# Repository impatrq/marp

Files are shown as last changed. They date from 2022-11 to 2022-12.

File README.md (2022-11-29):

<div align="center">

# Mechanical Aid Rehabilitation Prototype

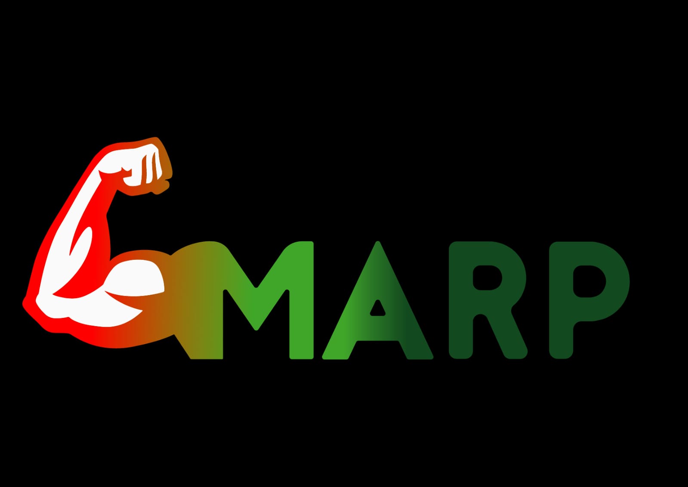
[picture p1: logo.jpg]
Logo proyecto


## ¿En qué consiste?

#### M.A.R.P (Mechanical Aid Rehabilitation Prototype) es un prototipo de exoesqueleto mecanico que consiste en un sistema de servomecanismos mediante el cual se obtiene un movimiento análogo a la contraccion de la mano. Estos son controlados por un microcontrolador. Tras recibir las señales de los musculos sensados por los electrodos colocados en el brazo, este activaria el protocolo correspondiente para realizar el movimiento deseado. En un principio este movimiento sera abrir y cerrar la mano.

## ¿Cuál es nuestro objetivo?

#### El objetivo de M.A.R.P. es asistir fisicamente a personas cuya capacidad motriz ha sido reducida, ya sea por haber sufrido daño nervioso y/o deterioro natural.

## ¿Quienes somos?

#### Somos un entusiasta grupo de 6 alumnos que se encuentran cursando el último año en la Escuela de Educación Secundaria Técnica N°7 (con especialidad en Aviónica) interesados en temas de medicina, biología y tecnología.

## Integrantes:

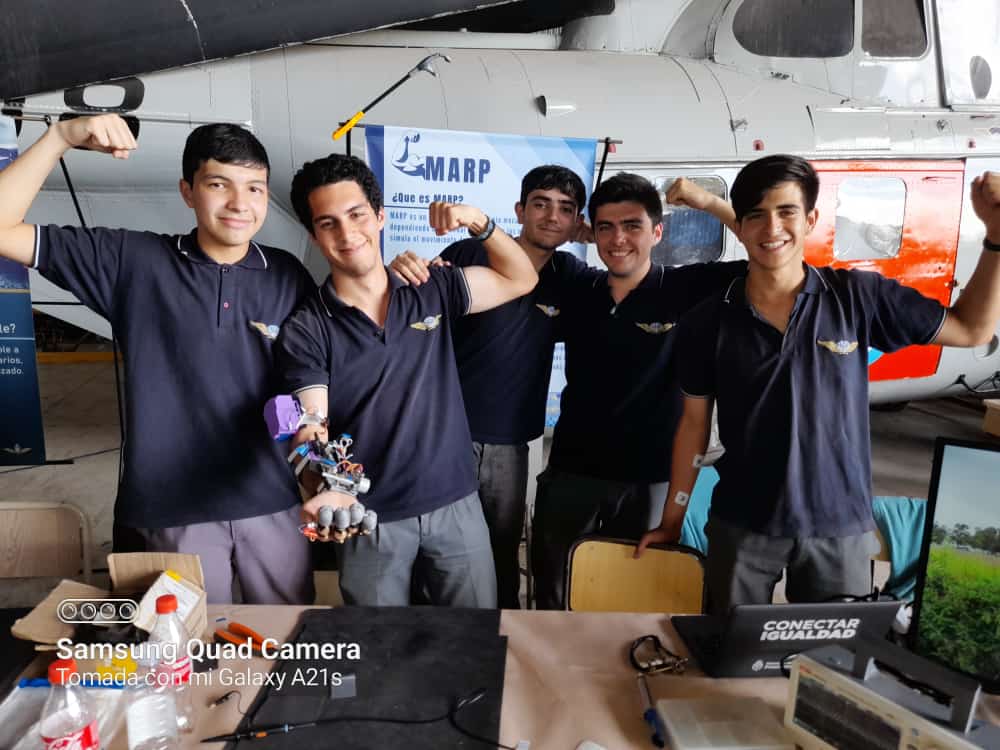
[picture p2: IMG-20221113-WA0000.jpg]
Integrantes


### NIETO, Matias Ezequiel
    📷 Instagram: matty_nieto
    📧 Email: mattynieto@gmail.com
### MONZÓN, Valentín Jeremias Daniel
    📷 Instagram: valen_monzii
    📧 Email: valenjereda10@gmail.com
### MONZON MATOS, Thomas Esteban 
    📷 Instagram: thomasmonzonmatos
    📧 Email: thomasemonzonm@gmail.com
### PIRILLO, Julian Dante 
    📷 Instagram: julianpirillo.03
    📧 Email: julipirillo@gmail.com
### FERNANDEZ IGLESIAS, Juan Ignacion
    📷 Instagram: juani.rvv
    📧 Email: juanignaciofernandez07@gmail.com
### LUPICA MARINI, Francisco Joaquin
    📷 Instagram: lupik_trq
    📧 Email: franciscolupica@gmail.com

## Contacto:
Cualquier duda la pueden consultar por:

    📧 Email: marpimpatrq@gmail.com
    📷 Instagram: marp_impatrq
    📞 Telefono: 1161022940

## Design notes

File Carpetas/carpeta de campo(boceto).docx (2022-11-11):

MARZO:

En este mes, presentamos una idea que ya teníamos desde el año pasado a nuestros profesores que era la de un exoesqueleto que ayudara a personas con poca o nula fuerza de agarre en labores cotidianos. Luego planteamos la idea actual del proyecto que sería un exoesqueleto capaz de ayudar a la rehabilitación de los nervios de la mano. Hubo cierta controversia debido a que uno de los profesores lo considero como uso ilegal de la medicina pero finalmente la idea fue aceptada y comenzamos a trabajar en el anteproyecto.

ABRIL:

En este mes se finalizo el anteproyecto anteproyecto, ya que había que finalizarlo para definir cuál sería nuestro proyecto (en el cual trabajaríamos el resto del año). Luego de varios debates e ideas, tanto para hablar del tema de costos hasta para pensar cómo funcionaría desde un punto de vista comercial, se pudo concluir la idea del exoesqueleto de mano. Antes de entregar el anteproyecto a nuestros profesores también dedicamos tiempo a hacer una investigación sobre las nociones básicas detrás de la obtención de señales electromiográficas. Esto incluiría como son producidas, de que magnitud son, en que consta el equipamiento encargado de recibirlas, como varían y según que, como poder aprovecharlas, etc. También investigamos y recibimos asesoramiento sobre el tipo de lesiones para las cuales el exoesqueleto sería útil incluyendo lesiones por daño nervioso, neuropatías periféricas o enfermedades neurodegenerativas e Incluso victimas de daño cerebral. Nuestro proyecto todavía recibía críticas por parte del profesor Bianco con respecto a su relación estrecha con la realización de procedimientos médicos sin ningún tipo de autorización o validez, pero el asunto quedo definitivamente zanjado para fin de mes al proponer nuestro proyecto como un prototipo a desarrollar mas que como un proyecto definitivo.

MAYO:

En este mes el anteproyecto ya fue aprobado y estábamos en condiciones de poder comenzar el proyecto. Empezamos a ver alternativas en internet sobre diferentes diseños, tanto del circuito de obtención de la señal como el exoesqueleto. Todos los circuitos que vimos para cumplir la función de obtener una señal clara de los músculos constaban de un amplificador diferencial de alta impedancia y bajo ruido con la siguiente estructura.

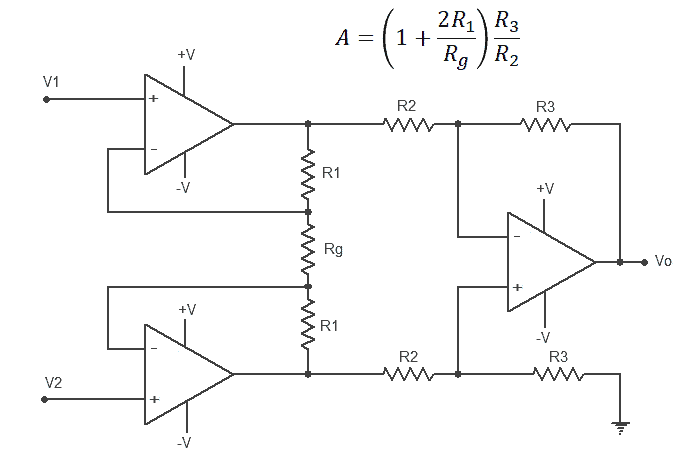
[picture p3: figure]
Instrumentation amplifier circuit diagram

La mayoría eran integrados INA106 el cual no pudimos conseguir por lo que tuvimos que reemplazarlo por un AD620. Este integrado fue diseñado específicamente para la obtención de señales electromiográficas. La ganancia de este amplificador se controla a través de una resistencia e hicimos los cálculos necesarios para obtener el valor que debería tener de manera que el AD620 tuviera una ganancia de 1000 veces el valor de la entrada. Esto se debe a que las señales del musculo son del orden de los 10 uV a los 100 mV, y para que funcione como condición para el Atmega328p que tenemos pensado utilizar, la señal final debe ser de 1V a 5V.

Para la etapa de filtrado tuvimos varios problemas. En parte se debía a que nadie sabía realmente cómo funcionaba un filtro y en parte porque en el lugar de trabajo donde en un futuro realizaríamos las primeras pruebas, había demasiado ruido. Al no saber el funcionamiento de los filtros nos limitamos a conseguir los materiales de uno de los circuitos que vimos y armarlo en un protoboard. También en este mes conseguimos los electrodos y la pasta conductora para iniciar las pruebas.

A pesar de que se nos recomendó trabajar por ahora únicamente en la obtención de la señal, se diseñaron bocetos de cómo podría llegar a ser el exoesqueleto. Dichos modelos incluyen un complejo sistema de engranajes para transformar el giro de un servo en el movimiento necesario para simular el cierre y apertura de la mano.

JUNIO:

En este mes se le empezó a dar importancia al tema del logo del proyecto. Se comenzó con bocetos en papel, y siguió con diseños completamente virtuales (todos se terminaron descartando).

Una vez armado sobre el protoboard nuestro primer circuito comenzamos con las pruebas. Tomó una cantidad absurda de tiempo invertido identificar ciertos errores que cometíamos en las mediciones sin estar conscientes de ello, ejemplo: no sabíamos que había que hacer una fuente partida, no sabíamos que la masa tenia que estar conectada a la masa del brazo. Tampoco sabíamos que el ruido en el ambiente podía ser tan fuerte como para atenuar la señal entregada y que eso se debía principalmente a la protoboard que actuaría como una antena y otros errores muy básicos, que en gran parte se deben a la falta de experiencia del grupo, que no vale la pena mencionar. Cambiamos el circuito pensando que los problemas se debían a la elección del mismo y primero intentamos hacer un tipo de filtro sallen key pasa bajo de Fc: 30Hz con la siguiente estructura.

(foto de filtro sallen key)

Comenzamos a entender mejor el principio de funcionamiento de un filtro por lo que sabíamos cómo calcular la frecuencia de corte y cómo funciona la atenuación de las señales. Sin embargo los filtros no funcionaron como deberían*

Nos limitamos a repetir la estructura del mismo filtro cuatro veces y lo que en proteus funcionaba a la perfección en la realidad funcionaba de manera muy distinta y no supimos por qué.

Sin embargo, tampoco sabemos por qué, cuando intentamos conectar al amplificador, únicamente un filtro Fc (el más básico que hay) pasa bajo con fc=100hz, se obtuvo el primer resultado positivo de todas las pruebas realizadas. Se apreció por primera vez una ligera pero constante variación en la señal obtenida a partir de los electrodos conectados al brazo del sujeto de prueba.

Desafortunadamente, la señal no era utilizable porque la variación era mínima, pero se amplificó, de los 10mV que suponemos que entrega el brazo, entregó 300 mV.

JULIO:

Este mes comenzamos a pensar y definir el sistema que utilizaríamos para mover los dedos de la mano, hicimos pruebas y comenzamos a diseñar el sistema en papel (el cual se cambio muchas veces). Acá fue cuando comenzamos a administrar la cuenta de instagram del proyecto para poder promocionarlo y que la gente lo conozca. Se reemplazó una parte del programador que ayudó a que los problemas de compatibilidad desaparecieran y se regresó a la programación.

También trabajamos junto al profesor Palmieri en la creación de una fuente partida pero en vez de utilizar las fuentes switching que usábamos antes utilizamos un transformador para obtener los +-5v que necesitábamos. Esto se decidió debido a que al trabajar con el profesor Arguello (y realizar nuestra primera prueba supervisada) nos advirtió que uno de los principales problemas de nuestro circuito era la propia fuente de alimentación. La propia masa de una fuente switching de por sí ya producía gran parte del ruido eléctrico. Fue ahí cuando supimos que debíamos utilizar o una batería o un transformador para evitar ese ruido.

(foto de la plaqueta)

El armado de las plaquetas y la prueba de la misma tuvieron varios inconvenientes. Entre ellos el hecho de que conectamos mal el regulador de la fuente (pensamos que un 7805 conectado al revés era lo mismo que un 7905) y quemamos varios fusibles, y también que las conexiones en si también estaban mal. Terminamos dejándolo de lado y planificamos la obtención de baterías electrolíticas para generar los +-5v.

Nuevamente volvimos a cambiar el circuito de filtrado esperando nuevamente que cambiarlo fuera suficiente para que dicho circuito funcionara.

(Foto del circuito)

Link de la página: https://www.dalcame.com/emg.html#.Y2JyHnbMLIU

Esta página también incluía información bastante detallada sobre el funcionamiento detrás de la electromiografía.

Esta vez sí nos tomamos el tiempo de aprender el funcionamiento detrás de cado de cada etapa del amplificador y filtrado.

Etapa de preamplificación:

(Foto amplificación)

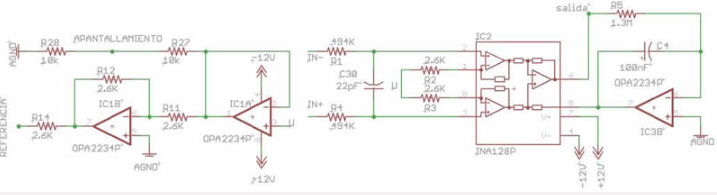
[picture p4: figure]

Esta etapa es la del AD620 pero también se incluía a la entrada positiva y negativa un filtro Rc. Esta vez el circuito incluía una etapa que era de apantallamiento que no sabemos para qué sirve pero aun así la incluimos. Se supone que aisla a la masa proveniente de los electrodos del resto del circuito. Obteniendo así supuestamente una señal con menos ruido y como son las pendientes de atenuación de la señal en base a la calidad del filtro

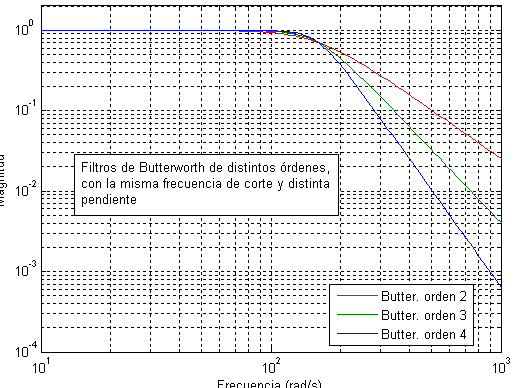
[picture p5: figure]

Primera etapa del filtro:

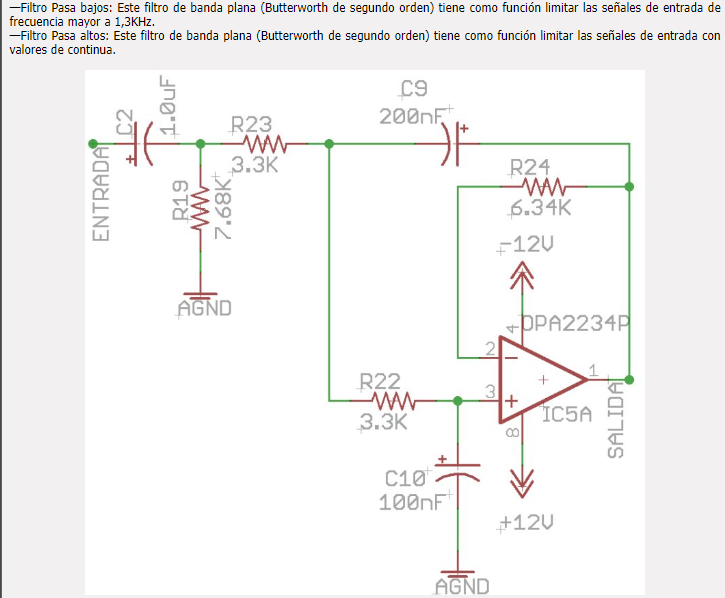
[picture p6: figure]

En el circuito a diferencia de los anteriores vistos tiene un filtro pasa bajos de 1.3KHz y pasa bajos de 1Hz butterworth. Y están diseñados de tal manera que la calidad del filtro sea mucho mayor

Esta era una de las posibles causas que anteriores filtros no funcionaran. Que la calidad del filtro varía según el valor de los elementos pasivos y que a pesar de que diferentes valores de los mismos podrían dar una frecuencia de corte similar el valor “Q”, que indica su calidad, no es el mismo. El valor para que el filtro sea de buena calidad de Q es 0.707.

Amplificacion

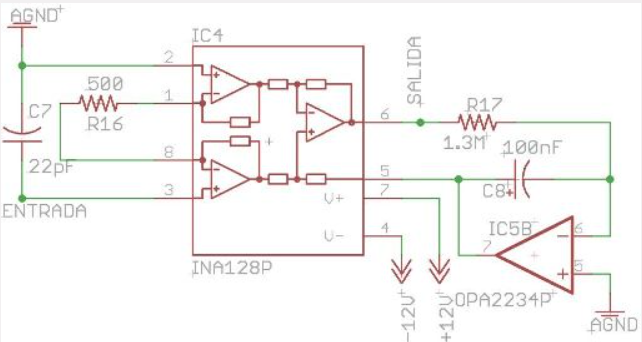
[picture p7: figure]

Este mes no se realizaron muchas pruebas por dos motivos: el primero serian las vacaciones de invierno, y el segundo es que hubo un retraso con el pedido de las baterías y decidimos dejar de realizar pruebas con las fuentes switching.

Como no podíamos hacer pruebas hasta obtener la batería le dedicamos mas tiempo a de una vez tener un modelo definitivo de la mano. Una vez obtenido supimos que gran parte de la misma tendría que ser diseñada en AutoCAD para su posterior impresión.

AGOSTO:

En este mes ya comenzamos a hacer la carcasa del proyecto en AutoCAD 3D, hicimos los soportes necesarios para las plaquetas, y el sistema de retracción de los dedos. Comenzamos la investigación sobre el programador y ya casi teníamos concluido el diseño logo.

SEPTIEMBRE:

En este mes continuamos con la obtención de materiales y conseguimos hacer funcionar el servo. También volvimos a cambiar por completo el circuito del filtro y con eso tuvimos que conseguir más materiales para su armado. Hicimos pruebas con este nuevo circuito y funcionaba cuando el input era un generador de seña. A la hora de conectarlo a un brazo no se podía obtener una buena señal (pésima relación signal to noise). También simulamos todo el circuito en proteus. En teoría funcionaria pero como resulta difícil agregar ruido en proteus no pudimos probar añadir más de una frecuencia. También imprimimos algunas de las partes de la mano.

OCTUBRE:

En este mes imprimimos en 3D las piezas de la carcasa en PLA y Flex. Como también rediseñar nuestro logo, y hacer el banner del proyecto para la exposición. También terminamos la programación del atmega328p para que mueva los servos que retraerán a los hilos, los cuales ayudaran a la mano a cerrarse y abrirse. A finales del mes se hizo la plaqueta del atmega328p en cobre, como también, la compra de un módulo con el AD620.

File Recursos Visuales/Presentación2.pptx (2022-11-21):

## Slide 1

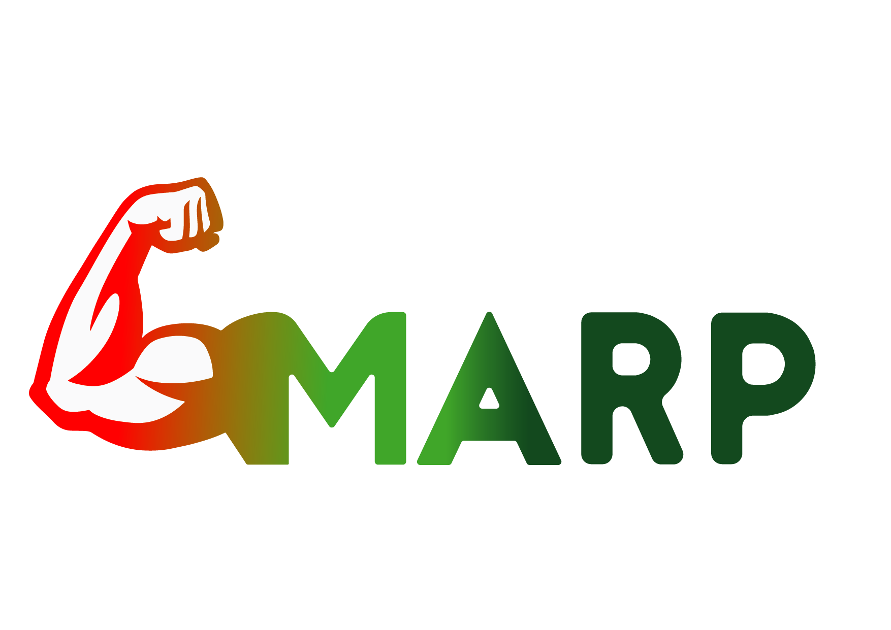
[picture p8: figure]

## ¿Qué es MARP?

- Mechanical Aid Rehabilitation Prototype (MARP) es un prototipo de instrumentación mecánica que se encarga de proveer la ayuda necesaria a la persona requerida cuya fuerza motriz fue debilitada por ciertos factores.

## ¿Cómo funciona?

- MARP utiliza señales eléctricas provocadas por la extensión y contracción muscular que son medidas con electrodos descartables
- Estas se envían a un amplificador y filtros para separar la señal del resto del ruido y hacerla detectable para el ATMEGA
- El Atmega328 P, es el corazón del proyecto, es quien da la orden a un motor Paso a Paso para que mueva los hilos de la carcaza y terminen por ayudar a contraer o extender los dedos de la mano

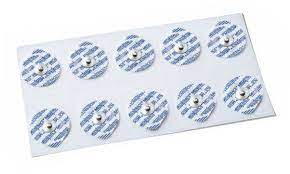
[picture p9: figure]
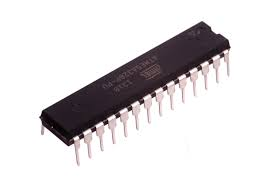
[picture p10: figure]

## Objetivo

- MARP se creó para brindar ayuda a las personas cuya movilidad o fuerza motriz fue reducida por un accidente u otros factores.
- Con MARP, los ejercicios de rehabilitación no serían obligatorios, ya que este produce la fuerza y efectos de igual manera para que el usuario pueda seguir con su vida cotidiana (La fuerza que brinda se irá reduciendo gradualmente hasta finalizar la rehabilitación)
- MARP no está diseñado para ser un añadido permanente al usuario, si no para apoyarlo en el transcurso de su recuperación.

## Procedimiento

Para la rehabilitación es necesario atravesar 4 fases:
- Fase de protección: confección de prótesis, manejo de edema y control del dolor.
- Fase restauradora: ejercicios de movilidad activa y de deslizamiento tendinoso.
- Fase de fortalecimiento: ejercicios de resistencia progresiva.
- Fase funcional: enfocada a recuperar habilidades para el desempeño de actividades de la vida diaria, tanto laborales como educativas.

## Integrantes

- MONZON MATOS, Thomas Esteban
- MONZÓN, Valentín Jeremias Daniel
- LUPICA MARINI , Francisco Joaquín
- NIETO, Matías Ezequiel
- PIRILLO, Julián Dante
- FERNÁNDEZ IGLESIAS, Juan Ignacio

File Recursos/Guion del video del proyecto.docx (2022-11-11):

Guion del video del proyecto:

Escena 1

- EXT. - Campo de aviónica superior.

Aparece peatón random (Francisco) mientras estaba bebiendo una Coca-Cola de 600 ml (mientras cruza panorámicamente la cámara fija), cuando de repente un balón de futbol impacta en dicha mano. Haciéndolo gemir de “dolor”.

- Fran: Arghhhhh. Mi mano, Hijos de p###.

En ese momento aparece caminado una persona (Juan) vestida con mercancía de marp/traje.

- Juan: Estas bien? No lo parece. Pero no te preocupes. Te presento marp.

*abre un maletín con el logo de marp (el interior no se verá desde el ángulo de la cámara)*

- Fran: Marp?

*comienza a desaparecer para luego desaparecer por completo*

Escena 2

- INT. – Sala secreta de MARP.

Aparece la persona (Fran) en una sala, confundido mira a su alrededor y encuentra en su delantera una mesa, con los integrantes de “MARP” (están usando mercancía de MARP) sentados en el lado opuesto de la mesa. Cuando la persona se da cuenta de su presencia un integrante dice:

- Valen: Bienvenido. ¿Te encuentras bien?

En ese momento se enfoca la cámara desde detrás de la persona un poco hacia arriba apuntando a la mesa, mientras se cae/rompe algo relacionado con MARP. Luego la cámara apunta a Fran:

- Fran: Creo que no, no puedo mover la mano.

La cámara sube un poco mostrando que todos están al lado de Fran.

- Nieto: Tenemos la solución a eso.
- Parillo: Te presentamos MARP (mientras saca un maletín con exoesqueleto)

Escena 3

- EXT. - Patio de la escuela

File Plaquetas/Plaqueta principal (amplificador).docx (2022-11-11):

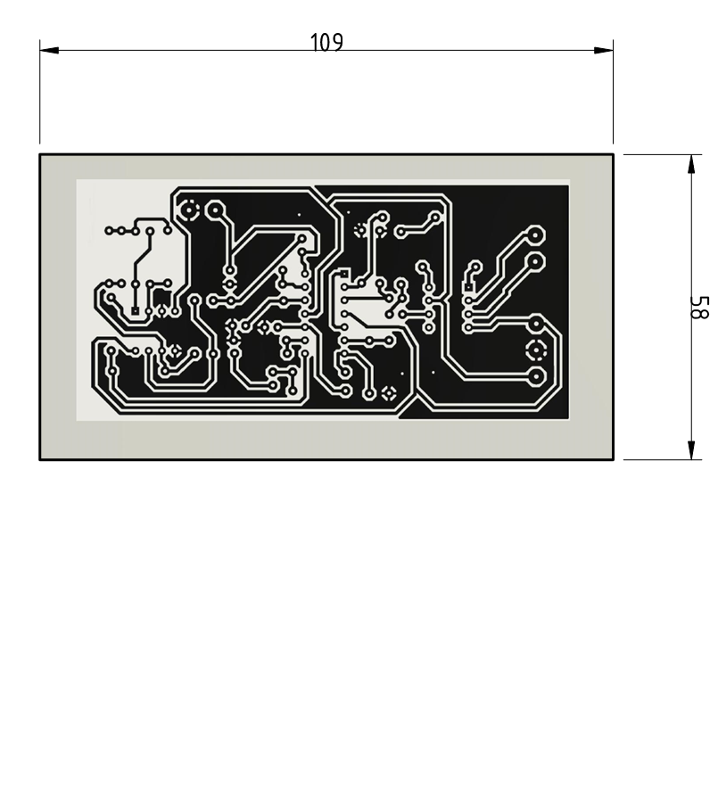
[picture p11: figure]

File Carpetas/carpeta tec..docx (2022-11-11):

Escuela de Educación Secundaria Técnica Nº7 TRQ

Proyecto final de 7mo

MECHANICAL
AID
REHABILITATION
PROTOTYPE

Integrantes:

FERNÁNDEZ, Juan Ignacio

LUPICA MARINI, Francisco Joaquín

MONZON MATOS, Thomas Esteban

MONZÓN, Valentín Jeremias Daniel

NIETO, Matías Ezequiel

PIRILLO, Julián Dante

## RESUMEN

Los diversos movimientos que podemos llegar a realizar con nuestro cuerpo tienen lugar como consecuencia de la transmisión de señales eléctricas a través de nuestro organismo. Estas señales tienen su origen en el sistema nervioso y son denominadas “potenciales de acción”. Sus características determinan el movimiento predeterminado que debe realizar un efector específico, concretamente la contracción o relajación de un músculo esquelético.

El proyecto presentado se basa en el análisis de dichas señales mediante el uso de la electromiografía superficial, colocando tres electrodos no intrusivos sobre unas localizaciones específicas del brazo que nos servirán como puntos de recogida de datos. La finalidad del proyecto consiste en la interpretación de las señales bioeléctricas transmitidas a los músculos que controlan los diversos movimientos de la mano. La dificultad del experimento reside, sin embargo, en la reducida amplitud de las señales a medir, generalmente del orden de mili voltios, muy inferior al orden del voltaje con el que trabajan los equipos electrónicos utilizados. Además, las interferencias intrínsecas y extrínsecas presentes durante el proceso dificultan la correcta interpretación de nuestras señales de trabajo. Por todo ello, hemos diseñado un circuito electrónico que nos permite acondicionar las señales tomadas con los electrodos, aplicando etapas de amplificación, filtrado, y rectificación. Tras el acondicionamiento de la señal, podemos proceder a la interpretación de los datos recogidos.

## 1. Introducción

Las diversas señales bioeléctricas que circulan a través de nuestro cuerpo pueden ser captadas y tratadas mediante circuitos electrónicos, fundamento en el cual se basan diversas técnicas biomédicas actuales. En el presente trabajo nos dedicamos a captar las señales mencionadas mediante electromiografía superficial, para posteriormente aplicar el debido tratamiento y acondicionamiento que nos permitan interpretar dichos estímulos. Para ello, hemos diseñado una placa de circuito impreso, y se han realizado dos pruebas: la primera con señales artificiales obtenidas a partir de un generador de funciones, y la segunda con señales bioeléctricas reales. Finalmente, mediante la aplicación de un código informático creado en la plataforma de Arduino, se procede a la interpretación de los movimientos básicos de apertura y cierre de la mano.

### 1.1. Objetivos y motivación

El proyecto realizado se ha llevado a cabo con los objetivos de comprobar el correcto tratamiento de las señales bioeléctricas mediante el uso del circuito impreso diseñado, y su posterior interpretación a través de la plataforma Arduino.

La intención del trabajo realizado consiste en diseñar un proyecto que sirva como base inicial de un sistema más complejo que pueda aplicarse en personas con alguna discapacidad motriz en la mano o poca fuerza de agarre. Para ello, vamos a analizar las señales que intervienen en los movimientos de la mano; y a partir de un movimiento característico se puede interpretar y traducir la señal eléctrica que genera este para luego transformarla en movimiento mecánico.

## 2. Marco biomédico

La comprensión del origen de las señales bioeléctricas que vamos a medir, y de cómo son capaces de transmitirse a través de nuestro organismo, nos ayudará a entender mejor como trabajan y de qué forma afectan a nuestros músculos. Por ello, empezamos definiendo el concepto de “potencial de acción” para posteriormente explicar su transmisión hasta los músculos, y la forma en la que actúan estos últimos. Para finalizar, se presenta la técnica de la electromiografía con sus características principales, y describimos el proceso de toma de señales detalladamente introduciendo el uso de los electrodos superficiales.

### 2.1. Potencial de acción

Para realizar cualquier acción, nuestro cuerpo debe ser capaz de reunir y evaluar los datos sensoriales que le proporcionamos con el fin de poder generar y enviar las órdenes necesarias para ejecutar dicha acción mediante la actuación de nuestros músculos. Estos últimos reciben el nombre de efectores, a los que también pertenecen otros grupos como las glándulas, y los podemos definir como tejidos u órganos que realizan funciones impuestas por el sistema nervioso o endocrino respectivamente. Para funcionar necesitan, por tanto, recibir unas órdenes provenientes de los sistemas mencionados, las cuales actuarán como un estímulo que se ha transmitido a través del cuerpo en forma de impulso eléctrico. Este impulso se denomina potencial de acción, y son las neuronas las encargadas de generar dicha señal eléctrica, en este caso neuronas de tipo eferente ya que transmiten señales de control a células externas a los centros integradores, como las musculares en este caso [4]. Para entender cómo se origina dicho potencial, debemos profundizar en este tema a nivel celular.

###### 2.1.1. Origen

Las diversas células que componen el cuerpo humano disponen de un potencial de membrana, el cual se define como la diferencia de potencial entre el exterior y el interior de dichas células. Esta diferencia de potencial es originada por el transporte de iones, principalmente de sodio (Na+) y potasio (K+), entre los dos lados de la membrana celular, de forma que existe un exceso de cargas positivas y negativas en el exterior y el interior de la célula respectivamente. Además, también encontramos iones de cloro (Cl-) en

ambos lados de la membrana y algunos aniones orgánicos en el interior, aportando ambos la negatividad a la célula, aunque no se tienen en cuenta para nuestra explicación al ser menos significativos. Generalmente, se establece una desigualdad en la distribución de iones que se da en el espacio a analizar, teniendo una mayor cantidad de sodio fuera de la célula y una mayor cantidad de potasio dentro de esta. El transporte de dichos iones depende de la permeabilidad de la membrana, mayor para el potasio, y del tipo de método utilizado para la transmisión, el cual se explica a continuación.

Por un lado, los iones pueden atravesar la membrana por canales iónicos proteicos que siempre se encuentran abiertos, lo que se conoce como transporte pasivo. El número de canales disponibles para el sodio es mucho menor que para el potasio, por ello caracterizamos a la membrana como más permeable a este último. Por otro lado, disponemos del transporte activo, en el cual una bomba de sodio-potasio es la encargada de iniciar y controlar el transporte de iones a través de la membrana (Figura 1). La diferencia principal entre ambos métodos radica en que el segundo necesita un aporte de energía para poder llevar a cabo su función, siendo esta aportación realizada mediante una molécula de ATP (adenosín trifosfato) que permite la fosforilación de la bomba. Cuando recibe dicha energía, permite el intercambio de iones entre el interior y el exterior de la célula, habiendo una mayor cantidad de iones de sodio que salen que la de iones de potasio que entran. Por tanto, el resultado final de los dos tipos de transporte es una desigualdad en la positividad de los dos lados (polarización), siendo el interior de la membrana menos positivo que el exterior [2].

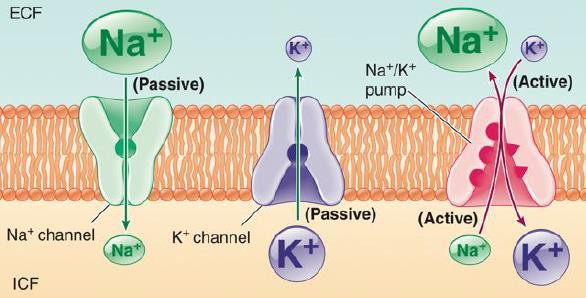
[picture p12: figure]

Figura 1. Transporte activo y pasivo de la membrana celular [2].

Por otro lado, la diferencia en la cantidad de los iones de cada elemento se ve contrarrestada por el movimiento de estos mismos iones, los cuales buscan mantener el gradiente de concentración en equilibrio. Sin embargo, cuando el gradiente eléctrico existente en un lado contrarresta al gradiente de concentración establecido en el otro lado, no se produce ninguna transmisión de iones, es decir, no existe un flujo neto de cargas. En ese momento se declara que el potencial de la membrana está en reposo, el cual corresponde al periodo de mínima actividad de la célula. El valor de dicho potencial es diferente para el sodio y el potasio, aunque en general se determina un valor intermedio de -70 mV. La negatividad de dicho potencial se debe a que estamos comparando el potencial del interior de la membrana con el del exterior, siendo este último considerado como el valor 0, por lo que al ser el interior menos positivo que el exterior, se declara como un potencial negativo. Una vez explicado todo esto, podemos pasar a definir el concepto que realmente nos interesa: el potencial de acción.

Cuando una célula recibe un estímulo suficientemente intenso, por ejemplo, una neurona que recibe un impulso nervioso procedente de otra neurona, se da paso a un conjunto de procesos encadenados que tienen lugar en la propia membrana celular, los cuales originaran el mencionado potencial de acción. Todo empieza con una despolarización celular, causada por la apertura de canales de compuerta en una región de la membrana que se origina debido al estímulo inicial. Estos canales son diferentes de los canales utilizados en el transporte pasivo, ya que están regulados por el impulso nervioso recibido. Como consecuencia, los iones de sodio empiezan a entrar a la célula para equilibrar el gradiente de concentración, hasta el punto de invertir el potencial al volverse el interior más positivo por la entrada de nuevos iones. En este momento, el potencial de membrana ha superado al umbral de voltaje (condición necesaria para generar el potencial buscado) y al potencial de reposo, experimentando una fase de potencial ascendente hasta un pico determinado, dando lugar al inicio del potencial de acción (Figura 2). Hay que añadir que el proceso de despolarización favorece la permeabilidad del sodio a través de la membrana, por lo que se produce un efecto de retroacción positiva al favorecerse el propio fenómeno a sí mismo.

Una vez alcanzado el potencial máximo en el pico, se produce un descenso en el valor de este debido a que las compuertas del potasio, cuya apertura y cierre son más lentos, se abren para permitir la transición de los iones de potasio al exterior de la célula para igualar

la concentración de estos. Además, las compuertas de sodio se cierran en ese mismo instante, por lo que se está reduciendo la positividad del interior de la membrana, originando un nuevo proceso de repolarización hasta alcanzar el valor del potencial de reposo. Puede darse además un proceso de hiperpolarización debido al cierre más lento de las compuertas del potasio, por lo que estaríamos extrayendo más iones positivos de la célula, haciendo su interior más negativo aún. Una vez se cierran los canales de potasio mencionados, el valor del potencial se reduce finalmente al del potencial de reposo gracias a que la bomba de sodio-potasio entra de nuevo en acción [2].

Figura 2. Evolución del potencial de membrana durante la generación de un potencial de acción [2].

Así es, por tanto, como se genera un potencial de acción, cuya función principal será la de transmitir la información aportada por las células a otro tipo de células o tejidos (p.ej. músculos o glándulas), y como consecuencia, modificar la distribución de las cargas eléctricas de las mismas. Cabe añadir que la intensidad de cualquier potencial de acción será independiente tanto de la magnitud del estímulo que lo ha generado, como de la

magnitud de la distancia del trayecto recorrido hasta llegar a su destino muscular [1]. El siguiente paso es, por tanto, analizar cómo se produce la transmisión de estos impulsos eléctricos.

###### 2.1.2. Transmisión

El sistema nervioso es el encargado de transmitir las órdenes a través de todo el cuerpo, exactamente el sistema nervioso periférico (SNP), compuesto por nervios que conectan el sistema nervioso central (SNC) con varias partes del organismo. El SNC está compuesto por el cerebro y la médula espinal principalmente, y su función consiste en generar y organizar las órdenes que posteriormente son enviadas a los efectores mediante las neuronas motoras, a partir de los estímulos recibidos de las neuronas sensitivas del cuerpo. Por otro lado, el SNP se puede dividir en dos subsistemas según el tipo de efectores que controle: el somático, que controla los músculos esqueléticos o estriados, los cuales conforman prácticamente la totalidad de nuestro cuerpo; y el autónomo, que controla los músculos lisos, las glándulas y el músculo cardíaco. Para nuestro caso, el somático es el que presenta un mayor interés ya que vamos a trabajar con músculos que podamos mover voluntariamente (músculos esqueléticos).

Toda esta transmisión y control sobre la información que proporcionamos a nuestro cuerpo es posible gracias a la sinapsis, que permite el contacto de las diversas neuronas con otras o con los propios efectores. Empezando por su origen, podemos establecer el cuerpo celular de una neurona como el inicio del impulso a analizar (Figura 3). A partir de este se transmite el potencial de acción a otras neuronas a través del axón, al cual se conecta mediante el cono axónico. La velocidad de conducción de dicho potencial a lo largo del axón celular es dependiente tanto del diámetro axónico y la temperatura (directamente proporcionales a la velocidad), como de la mielinización (la presencia de mielina en el axón aumenta la velocidad de propagación). Los impulsos viajan por el axón hasta llegar a las terminaciones presinápticas, liberando como consecuencia unas sustancias químicas denominadas neurotransmisores, los cuales pueden excitar o inhibir a las neuronas. Los neurotransmisores liberados alcanzan y afectan a las células postsinápticas mediante unas ramificaciones propias de estas denominadas dendritas. Para que se pueda llevar a cabo este proceso, es necesario un medio adecuado para el traslado de los mencionados neurotransmisores, el cual consiste en una zona característica

denominada sinapsis, por lo que a este fenómeno se le conoce como transmisión sináptica [2].

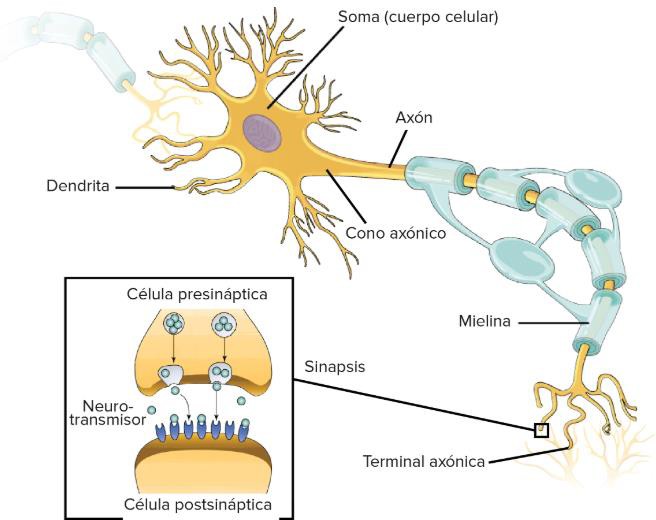
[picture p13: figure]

Figura 3. Transmisión sináptica en las terminaciones de una neurona [25].

El funcionamiento de la transmisión sináptica puede darse a través de señales eléctricas o químicas, siendo más frecuentes estas últimas, las cuales pueden ser excitadoras o inhibidoras de las células consiguientes. Para transmitir el potencial de acción, primero se debe transformar la señal eléctrica en una señal química mediante la liberación de neurotransmisores en los terminales pre sinápticos. Cuando estos alcanzan la membrana pos sináptica, se unen con receptores especializados que realizan una modificación eléctrica o química en la célula receptora como respuesta, desencadenando así un potencial sináptico. Este potencial puede ser excitatorio, el cual despolariza la membrana aumentando las posibilidades de que se desencadene un potencial de acción, o bien puede ser inhibitorio, el cual da lugar al proceso de hiperpolarización reduciendo así las posibilidades de que se genere el estímulo consiguiente. Por tanto, si los estímulos

excitadores originados por los neurotransmisores sobrepasan a los inhibidores, la neurona puede llegar a generar un potencial de acción de igual intensidad al original.

La señal bioeléctrica sigue avanzando hasta alcanzar los músculos esqueléticos (efectores), donde se genera un nuevo potencial de acción que se propaga despolarizando las membranas celulares y estimulando la contracción muscular. La relación entre la despolarización causada por el nuevo potencial y el fenómeno de la contracción del músculo es conocida como “acoplamiento excitación-contracción” [1]. Este fenómeno se explica más detalladamente en el siguiente apartado.

###### 2.1.3. Mecanismo muscular

Recordando lo explicado, podemos definir al conjunto de músculos como los órganos que nos permiten ejecutar las acciones que deseamos mediante la transmisión de órdenes generadas en nuestro sistema nervioso central. Las acciones musculares pueden ser de contracción o de extensión del músculo, aunque generalmente nos referimos al primer caso ya que los músculos sólo se extienden de forma pasiva, a diferencia de la contracción que normalmente es voluntaria. Cada músculo del cuerpo está inervado por una cantidad determinada de neuronas motoras, de forma que cada una de estas actúa sobre una gran cantidad de fibras musculares. Sin embargo, cada una de nuestras fibras musculares está inervada únicamente por una neurona motora, siendo dicha combinación definida como “unidad motora”.

Las fibras musculares están compuestas, además, por miofribillas cilíndricas y paralelas entre sí, que a su vez están cubiertas por una membrana celular denominada sarcolema (Figura 4). Dichas miofibrillas presentan diferentes bandas transversales, y contienen unos filamentos (miofilamentos) cuya función es la de generar la contracción del músculo. Los miofilamentos pueden ser de dos tipos: finos, compuestos por actina; o gruesos, compuestos por miosina. Este último tipo se caracteriza por disponer de unas proyecciones conocidas como puentes cruzados, los cuales, al recibir la célula muscular un estímulo determinado, interactúan con los miofilamentos finos y, gracias a la adición de una molécula de ATP, consiguen generar la fuerza que inicia la contracción [2]. Cabe aclarar que este proceso se rige por la denominada “teoría de los filamentos deslizantes”, según la cual los músculos no se contraen a causa de un acortamiento de los filamentos musculares, sino que el fenómeno de contracción es debido al deslizamiento de los dos

tipos de filamentos entre sí iniciado por la actuación de los mencionados puentes cruzados.

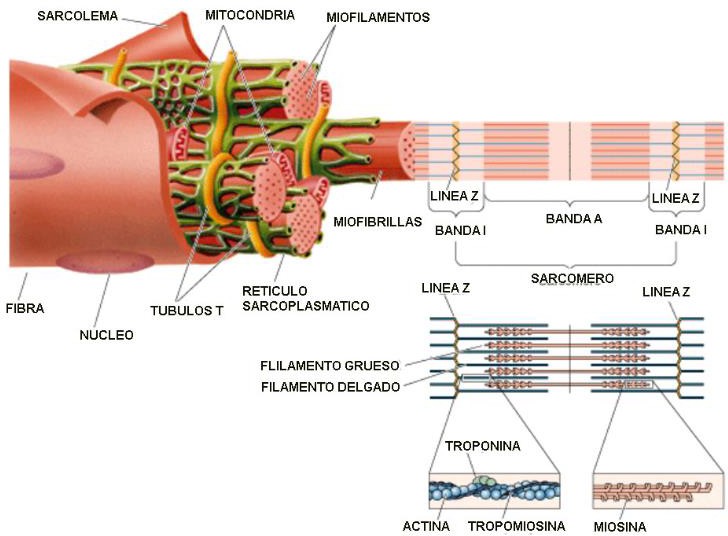
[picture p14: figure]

Figura 4. Estructura interna de la fibra muscular [26].

Finalmente, a causa de dicho deslizamiento conseguimos originar una tensión en el músculo que provoca el movimiento deseado. La magnitud de esta tensión viene determinada tanto por la frecuencia de generación de los potenciales de acción como de la longitud de la fibra muscular en el momento que recibe el estímulo.

### 2.2. Electromiografía

Una vez explicado el concepto de potencial de acción, podemos comprender mejor el uso de la electromiografía como técnica biomédica. La electromiografía (EMG) consiste en un procedimiento que permite diagnosticar tanto el estado de los músculos como de las células nerviosas (neuronas motoras) que los controlan mediante el análisis de las señales eléctricas que estas transmiten. Para captar dichas señales se utilizan unos dispositivos denominados electrodos, y según su forma de aplicación podemos distinguir entre varios tipos de electromiograma, como veremos más adelante. Una vez medidos los impulsos

eléctricos, las señales captadas son tratadas para poder interpretarlas ya sea mediante el uso de gráficos, sonidos o valores numéricos. El objetivo principal que suele tener dicha técnica en la medicina actual es detectar y ayudar a diagnosticar algún tipo de trastorno nervioso o muscular que pueda padecer el paciente [6].

###### 2.2.1. Señales EMG

Las señales medidas en un electromiograma como resultado de una contracción muscular se caracterizan por ser señales de muy baja amplitud, de 0.1 mV a 5 mV, y que se encuentran en un rango de frecuencias comprendido entre los valores 0.01 Hz, el cual puede considerarse como corriente continua, y 10 KHz (Tabla 1).

Tabla 1. Valores de los rangos de amplitud y frecuencia para diferentes tipos de técnicas biomédicas [7 (http://ocw.uv.es/ingenieria-y-arquitectura/1-5/ib_material/IB_T2_OCW.pdf)].

Las características de dichas señales vienen determinadas por diversos factores, como el tiempo y la intensidad de la contracción del músculo, la distancia entre el electrodo y la actividad muscular, las propiedades de la piel, o la calidad del equipo de trabajo. Desde que el impulso eléctrico es generado en el sistema nervioso central, hasta que se procede a la interpretación final de este, la señal se ha transmitido estando expuesta a las diversas interferencias que se pueden dar durante el proceso, principalmente ruidos. El ruido se puede definir como cualquier señal no deseada que se superpone a la señal útil analizada. Podemos diferenciar dos fuentes de este tipo de interferencias:

- Fuentes externas: generan interferencias que no proceden del cuerpo humano ni del equipo de medición. Destacan la interferencia de la red eléctrica, la electricidad estática debida a la fricción por movimiento, y la interferencia de radiofrecuencia debida a los equipos electrónicos del entorno del paciente.
- Fuentes internas: en este caso, las interferencias proceden del propio organismo o del equipo de medición. Estas pueden ser bioseñales ajenas y cercanas a la señal analizada (fenómeno de diafonía o crosstalk), interferencias debidas al contacto electrodo-piel, cambios bioquímicos en el organismo, o simplemente ruidos de los componentes eléctricos del propio circuito.

La posible presencia de estas interferencias, junto a la reducida amplitud de las bioseñales, dificulta notablemente la correcta interpretación de los datos recogidos. Es por ello por lo que necesitamos aplicar un pos tratamiento después de la medida de impulsos, buscando reducir la mayor cantidad de ruido a la vez que aumentamos la amplitud de la señal para poder trabajar con ella. Es necesario, por tanto, un buen equipo de medición con el que poder registrar las señales bioeléctricas con la mejor calidad posible.

###### 2.2.2. Sensores

En el ámbito tecnológico, normalmente existe la necesidad de convertir un tipo de magnitud, generalmente física (temperatura, desplazamiento…), en otro tipo de variable, ya sea una tensión o una corriente. Para poder realizar esta conversión, utilizamos unos dispositivos denominados sensores, entre los cuales podemos encontrar diferentes tipos para aplicaciones biomédicas. En este caso, los sensores que vamos a utilizar son los conocidos electrodos, cuya función principal consiste en convertir las corrientes iónicas provenientes del cuerpo humano en corrientes electrónicas que puedan ser utilizadas por los equipos convencionales. Entre los principales tipos, podemos diferencias los siguientes:

- Superficiales: se caracterizan por ser electrodos no intrusivos, es decir, no necesitan introducirse en la piel para poder captar las señales, únicamente deben estar en contacto con esta. Son utilizados principalmente en clínicas, y presentan una elevada impedancia de entrada. A esta impedancia hay que añadir la que presenta la propia piel (epidermis y dermis), por lo que la presencia de ruido será mayor. Por ello, en la mayoría de los casos suele utilizarse un gel conductor en el contacto electrodo-piel, de forma que las lecturas sean más estables y generemos menos ruido al reducir la impedancia. Incluso es recomendable, en caso de ser necesario, la realización de una ligera abrasión o punción de la piel para reducir la resistencia que presenta la misma al paso de las señales. Podemos encontrar diferentes tipos de electrodos superficiales:

- Metálicos: son los más empleados normalmente. Consisten en una placa metálica que se pone en contacto directo con la piel, utilizando una superficie adhesiva para mantener su posición. Generalmente se utilizan con un gel electrolítico que mejora la fijación del electrodo a la piel, pero que a su vez presentan una mayor impedancia que otros geles más conductores, por lo que resulta un inconveniente al generar más ruido.

-De succión: se suele utilizar para periodos cortos de tiempo. Disponen de una perilla de goma para obtener el vacío y fijar así el electrodo en su posición, por lo que no necesita de ningún adhesivo. Debido a esto, la concentración de sangre aumenta, y la conducción de la señal es mejor.

-Flotantes: consisten en unos electrodos con una cavidad circular que contiene el metal con una cantidad de gel electrolítico. Presentan la ventaja de repartir más uniformemente las cargas, y de evitar en mayor medida el movimiento relativo entre electrodo-electrolito, por lo que se generan menos interferencias.

-Flexibles: se adaptan mejor a las curvaturas de la superficie. Mejora el contacto con la piel, además de abarcar una mayor área de captación. Sin embargo, esto último puede llegar a ser un inconveniente al aumentar las posibilidades de introducir señales biológicas de músculos cercanos al analizado.

- Internos: las técnicas que utilizan este tipo de electrodos suelen ser más desagradables para el paciente debido a que, en este caso, debemos introducir los electrodos a través de la piel para ponerse en contacto con el medio interno. Generalmente consisten en una aguja de metal que, unida a un cable que transmite la información, se inserta directamente en el músculo. Hay algunas que disponen de terminaciones de anclaje para poder mantener el electrodo en una posición fija. La ventaja principal que presenta es la eliminación de la impedancia debida a los efectos de la piel, sin embargo, es más molesto que el método no intrusivo.
- Microelectrodos: este último tipo es menos utilizado debido a su gran dificultad de aplicación. Se utilizan para medir potenciales directamente en la membrana celular, por lo que es necesario disponer de un electrodo en el interior de la célula que permita obtener la diferencia de potencial respecto del exterior. Por ello, las dimensiones del

electrodo deben de ser muy reducidas, pero a su vez debe tener la resistencia suficiente como para poder atravesar la membrana celular.

Una vez analizados los diferentes tipos de electrodos con los que podemos trabajar, decidimos optar finalmente por los electrodos superficiales metálicos debido a que son no intrusivos, disponen de una mayor variedad de tamaños, y su utilización es relativamente sencilla.

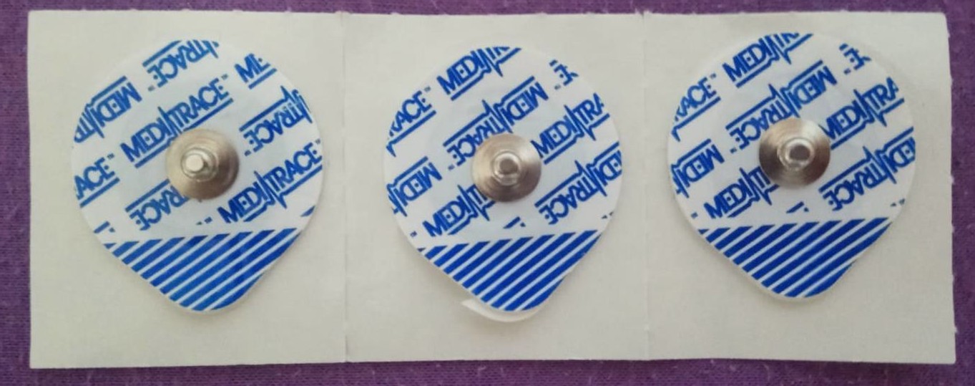
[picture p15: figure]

Figura 5. Electrodos superficiales empleados en la captación de señales.

Para este proyecto, se utilizan exactamente tres electrodos superficiales. Dos de ellos funcionan como sensores bipolares y se colocan sobre el músculo cuyas señales queremos analizar, con el fin de registrar la diferencia de potencial entre ambos. El tercer electrodo funciona como referencia, localizándose en una posición cercana al músculo, donde la actuación del potencial de acción sea mínima. La orientación del par de electrodos bipolar debe ser paralela a las fibras musculares sobre las que estén colocados, y es recomendable que la distancia entre ambos sensores no debe sobrepasar los 20 mm, ya que, según varios estudios, se consiguen señales de mayor amplitud limitando la distancia a ese máximo. Para el caso de músculos de tamaño reducido, la distancia máxima corresponde a ¼ de la longitud de la fibra muscular que compone el músculo analizado. Por lo referente a las características de los electrodos, la forma no influye notablemente en la recogida de señales EMG superficiales (EMGs), sin embargo, los electrodos circulares son preferibles generalmente. Por otro lado, el tamaño del electrodo sí que influye en el proceso, pudiendo variar desde 1 mm² a varios cm². La recomendación general es que el tamaño de los electrodos en la dirección de las fibras musculares sea inferior a 10 mm.

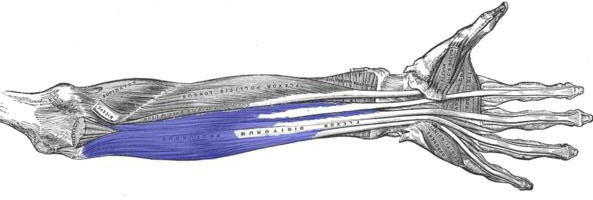
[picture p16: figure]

El último dato necesario es conocer la colocación de los electrodos para asegurar la correcta captación de las señales deseadas. Tras realizar un estudio anatómico del cuerpo humano, se concluye que el músculo que interviene mayormente en el movimiento de la mano es el denominado “flexor profundo de los dedos”, el cual se encuentra en el antebrazo (Figura 6). Dicho músculo tiene un tendón cuyas terminaciones se insertan en las falanges distales, inervando así los nervios mediano y cubital de la mano. Entre sus funciones encontramos tanto la flexión de la muñeca, como la flexión de las articulaciones metacarpofalángicas e interfalángicas, siendo por tanto capaz de controlar los movimientos principales de apertura y cierre de la mano.

Figura 6. Músculo flexor profundo de los dedos del brazo izquierdo.

Cabe añadir que, sin embargo, el movimiento del dedo pulgar no se incluye entre sus funciones, aunque no resulta un problema ya que podemos realizar nuestro análisis igualmente con los cuatro dedos restantes. De todas formas, el músculo que controla la flexión del pulgar (músculo flexor largo del pulgar) es cercano al músculo estudiado, por lo que las señales transmitidas a este primero pueden ser captadas de igual forma por los electrodos superficiales. Los sensores se localizan, por tanto, sobre el músculo mencionado, teniendo en cuenta las consideraciones mencionadas anteriormente. Dos de ellos se colocan alineados a una cierta distancia, de forma que podamos obtener la diferencia de potencial entre estos, mientras que el tercer electrodo de referencia se sitúa en el codo, al ser este una zona de baja actividad eléctrica (Figura 39). Es recomendable colocar los electrodos en zonas de baja masa muscular para reducir el ruido por superposición de señales.

Una vez se ha presentado todo el marco biomédico, a continuación, se explica el diseño del proceso de postratamiento aplicado a las señales recogidas.

## 3. Diseño del proceso

Para explicar el trabajo realizado, primero empezamos definiendo el objetivo específico de esta parte del proyecto, para posteriormente describir los diferentes componentes que se han utilizado y el diseño de cada una de las etapas. Finalmente, introducimos el código informático programado, y explicamos cómo se interpretan los datos recogidos.

### 3.1. Objetivo

El objetivo del proceso, como bien hemos expuesto al principio, es solo un paso necesario para conseguir el verdadero propósito práctico de este proyecto. Para ello, debemos diseñar un proceso que pueda transformar las señales bioeléctricas de nuestro cuerpo en otro tipo de señales con las que podamos trabajar. Para conseguir este objetivo previo, aplicamos etapas de amplificación, filtrado y rectificación para acondicionar la señal, obteniendo en cada etapa un valor de relación entre la variable de entrada y la de salida a la que denominamos ganancia, la cual representa la amplificación realizada. Dicha ganancia corresponde generalmente a un valor de voltaje, el cual se puede evaluar en V/V o en decibelios (valor logarítmico). Posteriormente, mediante la aplicación de un código informático, transformamos las respuestas del sistema en variables que puedan ser interpretadas.

### 3.2. Placa de circuito impreso

Para poder desarrollar el pos tratamiento utilizamos una placa de circuito impreso, generalmente conocida como PCB (Printed Circuit Board), la cual nos permite realizar las conexiones necesarias entre los diversos componentes electrónicos, permitiendo además una distribución más compacta y organizada de estos.

###### 3.2.1. Construcción de la PCB

Para empezar, partimos de una lámina de cobre reforzada con fibra de vidrio que nos sirve como soporte del circuito, la cual debe ser dimensionada en función del espacio que ocupa la totalidad del circuito. Antes que nada, por tanto, debemos disponer del diseño de nuestro conexionado o fotolito, el cual se ha implementado con el programa Proteus. Una vez disponemos de nuestro fotolito, preparamos unas láminas de plástico

en las que se imprime el diseño creado, para posteriormente poder transferirlo a una de las caras de nuestra placa dimensionada.

Figura 7. Diseño del fotolito implementado con el programa Proteus.

El siguiente paso es intercalar nuestra placa entre las láminas de plástico con nuestro circuito impreso. Cuando se asegure la correcta colocación, podemos introducirla en la insoladora, cuya función es imprimir el diseño de las láminas de plástico en nuestra placa aplicando una gran cantidad de luz a la vez que genera una depresión. Debemos de esperar alrededor de 2 minutos para obtener el resultado impreso.

Seguidamente, procedemos al revelado de la placa mediante la aplicación de sosa cáustica, generada como resultado de mezclar un líquido constituido por un revelador de placa positiva y una cantidad determinada de agua. Debemos sumergir la placa en dicha solución y removerla con cuidado, hasta que podamos distinguir las diversas conexiones de nuestro circuito.

A continuación, atacamos ambas superficies con un ácido (cloruro férrico) que nos ayuda a diluir todo el cobre restante que no pertenezca a las conexiones del diseño original. Al igual que el paso anterior, debemos remover la placa en el fluido, pero teniendo cuidado de que el ataque con ácido no sea excesivo. Al acabar, se debe lavar bien la placa con agua para finalmente frotarla con alcohol, con lo que conseguimos eliminar el film que protegía al cobre del conexionado del ácido aplicado anteriormente. De esta forma, obtenemos nuestra placa con un circuito impreso en una de sus caras. Lo único que falta es proceder al taladrado de la placa para la posterior colocación y soldadura de cada uno de los componentes que constituyen el circuito de trabajo.

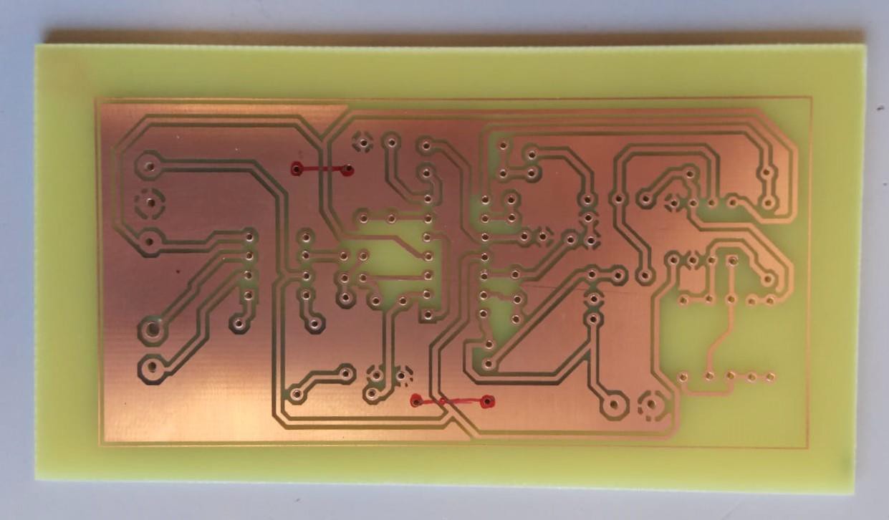
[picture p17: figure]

Figura 8. Placa de circuito impreso después del taladrado.

###### 3.2.2. Componentes eléctricos y electrónicos

Entre los componentes utilizados en nuestra placa de circuito impreso, podemos encontrar:

      - Resistor: consiste en un elemento pasivo que se opone al paso de la corriente eléctrica a través de un conductor. Su funcionamiento se basa en el efecto Joule, y su unidad de medida es el ohm (Ω). Se utiliza dicho componente en cada una de las etapas del proceso, habiendo realizado previamente el cálculo de los valores correspondientes. Sus tolerancias influyen, además, sobre las ganancias de las diversas etapas que constituyen.
      - Condensador: consiste en un elemento pasivo capaz de almacenar una cierta cantidad de energía eléctrica para posteriormente proporcionarla a un circuito. Está constituido generalmente por dos láminas conductoras intercaladas por un material no conductor o dieléctrico, y su unidad de medida es el faradio (F). Los tipos más utilizados en general son los cerámicos y los electrolíticos, destacando estos últimos por presentar polaridad. Dicho componente, en conjunto con las resistencias, son de gran utilidad en las etapas de filtrado, las cuales son explicadas más adelante. De la misma forma, debemos calcular previamente los valores de cada uno de los condensadores utilizados.
      - Diodo: consiste en un elemento activo que funciona como un semiconductor, el cual permite el paso de la corriente eléctrica a través de él en una sola dirección, provocando una caída de tensión de entre 0.6-0.7 V. Dispone de dos terminales, ánodo y cátodo, cuya disposición en el circuito determina el tipo de polarización del diodo, ya sea directa o indirecta. Debido a sus características, suele utilizarse para diversas funciones en la electrónica, y en nuestro caso, nos ayuda a realizar la etapa de rectificación correctamente. Entre los diferentes modelos de diodos, hemos elegido el “1N4148” debido a su fiabilidad y a su reducido coste de producción.
      - Amplificador: consiste en un sistema electrónico que ofrece una señal de salida de mayor potencia que la de entrada, respetando en todo lo posible la linealidad de dicha señal. En otras palabras, la señal de salida obtenida debe mantener los parámetros característicos de la excitación de entrada aun estando amplificada. Existe una gran diversidad de amplificadores utilizados para diversas funciones, pero en nuestro caso utilizamos solo dos tipos:
- Amplificador operacional: se trata de un circuito integrado que dispone de dos entradas (inversora/no inversora) y una salida, por la cual proporciona la señal modificada. Presenta una elevada impedancia de entrada, con lo que evita en mayor grado la presencia de interferencias, pero una impedancia de salida muy reducida. Su diseño permite aplicar o no una realimentación, consiguiendo así una mayor estabilidad gracias a la posibilidad de controlar la ganancia del amplificador mediante el uso de componentes externos en la realimentación. Generalmente, los encapsulados de estos amplificadores disponen de 8, 12 o 14 pines, cada uno con una función predeterminada, entre los cuales encontramos los terminales de alimentación del dispositivo. Es muy utilizado en la electrónica actual debido a su fiabilidad, su manejabilidad y su precio económico. En este caso, hemos optado por dos modelos de encapsulados diferentes para poder optimizar la cantidad de componentes y el tamaño de la placa. Se trata del modelo TL082, cuyo encapsulado dispone de dos amplificadores operacionales (U2A y U2B), y el modelo TL084, el cual dispone de cuatro amplificadores operacionales (U6A, U6B, U6C y U6D). Ambos comparten características similares, siendo las más importantes para el proyecto las siguientes [28][29]:
  - Voltaje de alimentación máximo: ±18V.
  - Rango de ganancia: 1-200 V/mV.
  - Potencia máxima disipada: 680 mW.
  - Tensión de offset: 3mV.
  - Common Mode Rejection Ratio (CMRR): 86 dB.
  - Ancho de banda: 3 MHz.
  - Resistencia de entrada: 1 TΩ.

Como podemos observar, entre las características de estos modelos destacan una elevada impedancia de entrada, un consumo de potencia reducido, y un ancho de banda superior al de las señales de trabajo. Por otro lado, la tensión de offset es de tan solo unos pocos mili voltios, cosa que nos conviene ya que cuanto más reducido sea este valor, menos posibilidades hay de variar el voltaje de salida (error de offset). Por último, el valor del CMRR debería de ser algo más elevado para asegurar eliminar la mayor cantidad de ruido posible, sin embargo, es suficiente para poder obtener una señal correctamente acondicionada [3]. Cabe añadir que las amplificaciones que aplicamos con dichos dispositivos son de orden reducido en comparación con otros modelos de amplificadores, por lo que el rango de ganancias especificado es más que suficiente.

Figura 9. Conexiones de los pines de los encapsulados TL082 a la izquierda [29], y TL084 a la derecha [28].

- Amplificador diferencial: podemos definir este componente como un amplificador operacional cuya configuración le permite amplificar la diferencia de voltaje o corriente existente entre las dos señales que recibe por cada una de sus entradas,

obteniendo como resultado una señal de salida que está en fase con estas. Esta configuración permite tratar mejor con los problemas relacionados con la amplificación de ruido o, en general, de cualquier señal común a ambas entradas que pueda influir negativamente en los resultados. Sin embargo, presenta los inconvenientes de tener un valor reducido de impedancia de entrada, además de dificultar el control sobre la ganancia del dispositivo. Como solución, se ha optado por utilizar una variante denominada amplificador diferencial de instrumentación, el cual consiste en un circuito integrado constituido principalmente por amplificadores operacionales, y que presenta una elevada impedancia de entrada, además de permitir controlar el valor de la ganancia a través de una resistencia variable. En este caso, se ha elegido el modelo de amplificador diferencial de instrumentación AD620, cuyas características son las siguientes [27]:

  - Voltaje de alimentación máximo: ±18V.
  - Rango de ganancia: 1-10000 V/V.
  - Potencia máxima disipada: 650 mW.
  - Tensión de offset: 50 µV.
  - Common Mode Rejection Ratio (CMRR): 100 dB.
  - Ancho de banda: 120 KHz.
  - Resistencia de entrada: 1 GΩ.

Como podemos observar, al igual que en el caso del TL081, entre las características de este modelo destacan una elevada impedancia de entrada, un consumo de potencia reducido, y un ancho de banda superior al de las señales de trabajo. Por otro lado, la tensión de offset es incluso menor, del orden de micro voltios, por lo que tenemos todavía un error de offset más pequeño [3]. El valor del CMRR es adecuado para las señales con las que tratamos, y el rango de ganancias es más que suficiente para trabajar con las amplificaciones requeridas. Por último, añadir que dicho modelo se caracteriza por disponer de una alta precisión, la cual nos permite trabajar con señales de amplitud muy reducida. Por todo esto, finalmente hemos optado por el modelo de amplificador diferencial de instrumentación AD620.

Figura 10. Conexiones de los pines del amplificador diferencial de instrumentación AD620 [27].

      - Bloque terminal: consisten en dispositivos a los que se puede conectar diversos cables con el propósito de establecer unas conexiones más seguras y de una forma más organizada con otros terminales. Suele disponer de dos o más puntos de conexión aislados entre sí, los cuales pueden ser ajustados mediante tornillos, por lo que resultan fáciles de usar. En nuestro caso, utilizamos bloques terminales de dos y tres puntos de conexión para realizar las conexiones entre la placa y los electrodos, la fuente de alimentación, y el conector que transmitirá la señal final de trabajo.

En la Tabla 2 podemos observar la lista de todos los componentes que utilizamos en nuestra placa de circuito impreso, cuya disposición se muestra en la Figura 11.

Figura 11. Disposición de los componentes eléctricos y electrónicos sobre la placa de circuito impreso.

Componente | Especificaciones | Cantidad
Bloque terminal | 2 puntos de conexión | 2
| 3 puntos de conexión | 1
Amplificador operacional | Encapsulado TL082 | 1
| Encapsulado TL084 | 1
Amplificador diferencial de instrumentación | Modelo AD620 | 1
Condensador | 6.8 µF (electrolítico) | 2
| 0.68 µF (cerámico) | 2
| 0.068 µF (cerámico) | 2
Diodo | Modelo 1N4148 | 2
Resistencia | 100 Ω | 1
| 390 Ω | 2
| 680 Ω | 3
| 1 KΩ | 6
| 1.2 KΩ | 2
| 3.3 KΩ | 1
| 10 KΩ | 1
| 12 KΩ | 2
| 100 KΩ | 1
| 220 KΩ | 2

Tabla 2. Cuadro resumen de todos los componentes que constituyen la placa de circuito impreso.

Los valores de cada una de las resistencias y de los condensadores se calculan en los siguientes apartados en función de las ganancias de cada etapa. Cabe añadir que, durante la realización del montaje de componentes, han aparecido ciertos problemas de conexionado en la placa de circuito impreso, pero han sido solucionados mediante la aplicación de puentes con cables. Finalmente, utilizamos un multímetro para comprobar que las conexiones entre los diversos terminales se han realizado correctamente.

### 3.3. Etapas del proceso

En este apartado, únicamente nos centramos en describir las diferentes etapas correspondientes al tratamiento de señales, las cuales están diseñadas en función de las características que requiere nuestra señal final de trabajo.

El proyecto se divide en un total de 6 etapas, cada una de ellas con una función específica dentro del proceso general. El resultado que queremos obtener a partir de la excitación de entrada es una señal eléctrica amplificada y libre de interferencias, de forma que la posterior interpretación de esta resulte lo menos complicada posible. Según la Tabla 1,

los impulsos eléctricos a tratar tienen una amplitud máxima de 5 mV aproximadamente, por lo que debemos realizar una gran amplificación para llegar al orden de voltaje con el que trabajan nuestros equipos. En este caso, hay que considerar que utilizamos una placa Arduino para la interpretación de los datos, y que dicha placa trabaja con señales de 5 V máximo. Por lo tanto, hemos decidido diseñar el circuito en función de obtener una ganancia total de aproximadamente 1000 V/V, preferiblemente inferior a este, ya que de esta forma nos aseguramos de que cualquier bioseñal acondicionada pueda entrar en el rango de lectura de nuestra placa Arduino.

Las etapas, a su vez, se pueden diferenciar en dos fases: una primera fase de acondicionamiento, en la cual aplicamos una etapa de amplificación diferencial, seguida de un filtrado paso-alto, otra amplificación de menor orden, y finalmente un filtrado paso- bajo; y una segunda etapa de obtención de la envolvente de la señal acondicionada, en la cual aplicamos una rectificación de onda completa, y otro filtrado paso-bajo. Como para los procesos de filtrado y rectificación se emplea un amplificador operacional, podemos definir a los filtros y al rectificador utilizados como activos. Al final de este apartado, hemos añadido un cuadro resumen de todos los ciclos con las ganancias correspondientes a cada uno y sus funciones principales. A continuación, describimos más detalladamente cada una de las etapas mencionadas.

###### 3.3.1. Etapa de amplificación diferencial

El primer paso a realizar para la fase de acondicionamiento es captar la diferencia de voltaje mediante el uso de los dos electrodos superficiales colocados sobre el músculo efector. Los extremos de ambos sensores están conectados a cada una de las entradas de un amplificador diferencial, en nuestro caso el AD620, mientras que el electrodo de referencia está en contacto con otro terminal, el cual se conecta a la toma a tierra. Podemos apreciarlo mejor en el siguiente esquema (Figura 12):

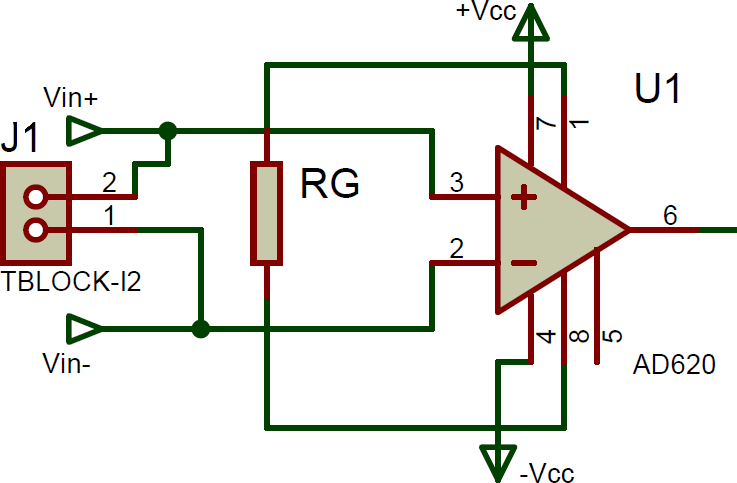
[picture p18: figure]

Figura 12. Esquema de las conexiones del dispositivo AD620 de la etapa de amplificación diferencial.

###### 3.3.2. Etapa de filtrado paso-alto

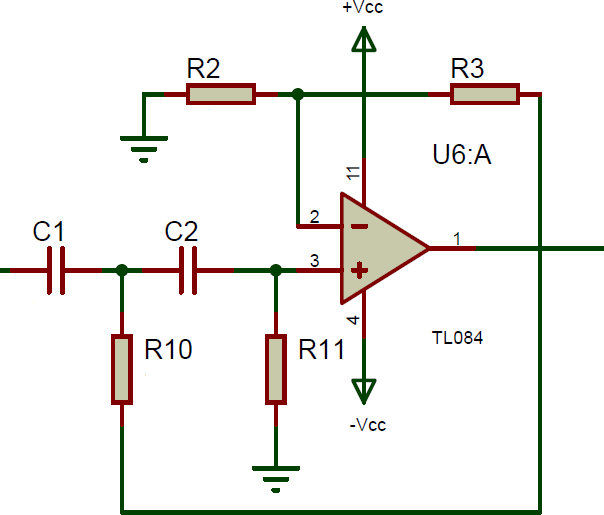
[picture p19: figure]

La segunda etapa consiste en un filtrado paso-alto de la señal, la cual tiene la función de atenuar las señales cuyas frecuencias se sitúen por debajo de una determinada frecuencia de corte. Esto nos permite eliminar tanto ruidos indeseados como señales de baja frecuencia que no sean relevantes para el proceso. Como frecuencia de corte hemos elegido un valor de 1 Hz, ya que la frecuencia mínima de las señales bioeléctricas es prácticamente nula (Tabla 1). Para ello, utilizamos una tipología de filtro denominada Sallen-Key, en este caso de segundo orden, ya que está compuesto por dos elementos reactivos (condensadores). En un principio nos interesa que el orden del filtro no sea elevado, ya que significaría disponer de una mayor cantidad de componentes y, por consiguiente, más fuentes de ruido interno. Además, se aplica la simplificación de utilizar un par de condensadores y de resistencias del mismo valor, con lo que conseguiremos reducir los cálculos a realizar [13]. Entre los diversos tipos de respuestas en frecuencia con los que podemos trabajar, hemos decidido que el más conveniente para este filtro es la aproximación Butterworth, ya que se caracteriza por ser prácticamente constante en la banda de paso y presentar una caída suave a mayores frecuencias, de forma que nos permite trabajar con valores que varíen lo menos posible con la frecuencia [12 (http://ocw.uv.es/ingenieria-y-arquitectura/filtros-digitales/tema_2._revision_de_los_tipos_de_filtros_analogicos_mas_comunes.pdf)]. En la Figura 13 podemos apreciar la configuración del filtro utilizado:

Figura 13. Esquema de las conexiones del amplificador operacional U6A (TL084) de la etapa de filtrado paso-alto.

El principio de funcionamiento de este tipo de filtros se basa en la diferencia entre el comportamiento resistivo de los componentes de un filtro RC ante señales de diferente frecuencia. Los filtros RC se caracterizan por estar constituidos por un condensador y una resistencia como mínimo, siendo la cantidad de elementos reactivos (inductores y condensadores) la que indica el orden del filtro. Por un lado, el condensador funciona como un elemento que ofrece una resistencia elevada a las señales de baja frecuencia o DC, mientras que, por otro lado, la resistencia funciona como un elemento que presenta una mayor oposición a las señales de frecuencias elevadas. Por lo tanto, según la distribución de estos componentes en el circuito, estaremos formando un filtro paso-alto o paso-bajo. En esta etapa, aplicamos un filtrado paso-alto, por lo que debemos colocar los condensadores en serie con la entrada del amplificador operacional utilizado para permitir así el paso de las señales de alta frecuencia. Las señales de baja frecuencia que consiguen pasar a través de los condensadores circulan a través de una resistencia, la cual les presenta menor oposición, hacia una toma de tierra, de forma que su intervención en el proceso de filtrado es mínima [9 (http://www.learningaboutelectronics.com/Articulos/Filtro-paso-alto.php)].

###### 3.3.3. Etapa de amplificación

El siguiente proceso consiste en amplificar la señal obtenida después de atenuar las excitaciones de baja frecuencia, con lo que conseguimos reducir las posibilidades de superponer interferencias no deseadas, mayormente ruidos, a nuestra señal de trabajo. Para esta segunda amplificación utilizamos uno de los amplificadores operacionales que nos proporciona el encapsulado TL084, exactamente el U6B. Al igual que en las etapas de filtrado, empleamos una configuración del dispositivo no inversora, conectando la entrada inversora a tierra, de forma que la señal de salida amplificada se encuentre en fase con la señal de entrada. En este caso, hemos aplicado una realimentación negativa, la cual nos permite modificar las impedancias de entrada y salida, además de estabilizar la ganancia del circuito y reducir la distorsión de la señal generada [30 (http://www.iuma.ulpgc.es/~lopez/Circuitos%20analogicos/apuntes4.pdf)]. El esquema de esta etapa es el siguiente:

Figura 14. Esquema de las conexiones del amplificador operacional U6B (TL084) de la etapa de amplificación.

Sin embargo, como ya hemos mencionado anteriormente, nuestra forma de proceder va a consistir en predefinir un valor de ganancia de la etapa para obtener posteriormente el valor de las resistencias que necesitamos en este proceso. Para ello, estimamos un valor de amplificación en función de la ganancia total que deseamos para el circuito, la cual debe estar cerca de 1000 V/V.

Tras realizar varias iteraciones, hemos decidido que la mejor forma de realizar la amplificación es eligiendo unas resistencias de R4 = 3.3 KΩ y R5 = 10 KΩ, de forma que la ganancia final de esta etapa resulta aproximadamente de GA = 4 V/V, siendo el rango de ganancias de [3.74; 4.35] V/V. Al tomar estos valores, y sabiendo que la amplificación de la siguiente etapa de filtrado paso-bajo (K’) es la misma que para el filtrado paso-alto anterior (K), podemos calcular la ganancia total del sistema como:

GT = GADI · K · GA · K’ = 74 · 1.5858 · 4 · 1.5858 = 744 V/V (10)

Con este valor final, conseguimos amplificar las señales bioeléctricas del orden de milivoltios a voltios, asegurando además que dichas señales acondicionadas se encuentren en el rango de trabajo de nuestra placa Arduino.

###### 3.3.4. Etapa de filtrado paso-bajo I

La cuarta etapa consiste en un filtrado paso-bajo de la señal, la cual tiene la función de atenuar las señales cuyas frecuencias se sitúen por encima de una determinada frecuencia de corte. La aplicación de este proceso en conjunto a la etapa anterior de filtrado conforma un filtro paso banda, el cual únicamente permite el paso a señales cuyas frecuencias se sitúen entre los límites establecidos por las frecuencias de corte de ambos filtros. De esta forma, podemos elegir el rango de frecuencias con el que queremos trabajar.

En este caso, la frecuencia de corte que hemos seleccionado es de 2 KHz, ya que representa la frecuencia típica de transmisión de los potenciales de acción [7 (http://ocw.uv.es/ingenieria-y-arquitectura/1-5/ib_material/IB_T2_OCW.pdf)]. Para ello, al igual que en el filtrado anterior, se utiliza la tipología de filtro Sallen-Key de segundo orden, aplicando la correspondiente simplificación de utilizar un par de condensadores y de resistencias del mismo valor [13 (http://www.ti.com/lit/an/sloa024b/sloa024b.pdf)]. Igualmente, nos interesa trabajar con una respuesta del tipo Butterworth para que los valores varíen lo menos posible con la frecuencia [12 (http://ocw.uv.es/ingenieria-y-arquitectura/filtros-digitales/tema_2._revision_de_los_tipos_de_filtros_analogicos_mas_comunes.pdf)]. En la siguiente imagen (Figura 16) podemos apreciar la configuración del filtro utilizado:

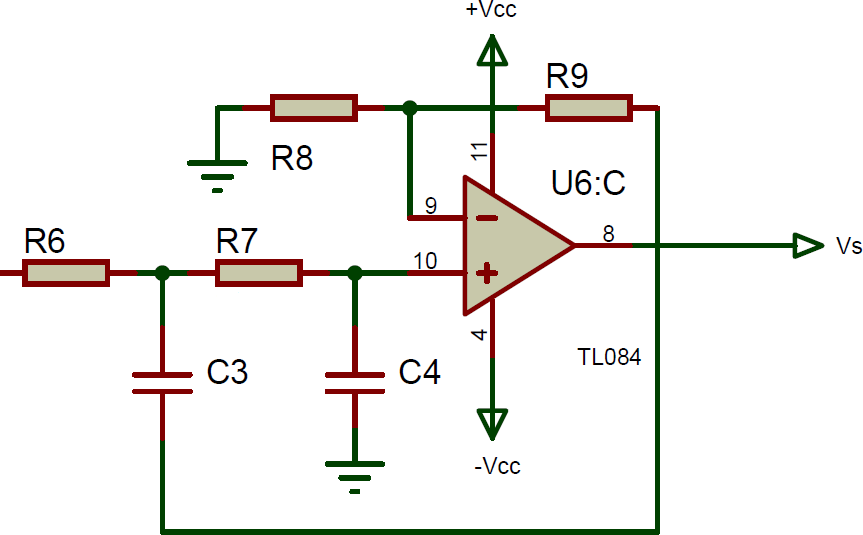
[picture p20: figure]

Figura 16. Esquema de las conexiones del amplificador operacional U6C (TL084) de la etapa de filtrado paso-bajo I.

###### 3.3.5. Etapa de rectificación

El siguiente paso que debemos realizar tras la fase de acondicionamiento es obtener la envolvente característica de la señal de trabajo que represente las contracciones musculares analizadas. Para ello, empezamos por describir la primera etapa de esta fase, la cual consiste en una rectificación de onda completa.

Cuando hablamos de rectificadores nos referimos a una configuración de circuito cuya utilidad se basa en la propiedad que poseen los diodos de permitir el paso de la corriente en un único sentido. Gracias a esto, podemos conseguir cambiar la forma de una señal de morfología alterna a una de señal continua, pero sin aplicar ninguna amplificación [33]. Existen dos tipos principales de rectificadores [32]:

o Media onda: su función es eliminar uno de los semiciclos, positivo o negativo, de la señal alterna de entrada en función de la polarización de los diodos que constituyen el circuito. De esta forma, se representan únicamente los semiciclos positivos o negativos, describiendo a su vez respuestas de amplitud nula que corresponden a los semiciclos de polaridad opuesta.

- Onda completa o doble onda: su funcionamiento es similar al rectificador de media onda, con la diferencia de que, en este caso, el circuito es capaz de convertir todos los semiciclos de la señal de entrada en una señal de salida de una sola polaridad. Es el tipo de rectificador más utilizado, y existen diversas maneras de implementarlo.

Sin embargo, las configuraciones típicas de estas dos clases de circuitos rectificadores presentan el inconveniente de no trabajar adecuadamente con señales de baja amplitud, debido principalmente a la presencia de diodos y su consecuente caída de voltaje, la cual reduce drásticamente la amplitud de trabajo. Es por ello por lo que, como solución a dicho problema, hemos decidido utilizar un tipo de circuito denominado “rectificador de precisión”, en este caso de onda completa. El motivo principal para escoger esta clase de rectificadores es que presentan la gran ventaja de poder trabajar con señales de amplitud muy reducida, a diferencia de los descritos anteriormente, y, además, al estar constituidos por amplificadores operacionales, evita el problema de la caída de voltaje provocada por los diodos [34 (http://www.geocities.ws/raguma_006/descargas/rectificador_de_presicion.pdf)]. El esquema de la configuración empleada es el siguiente:

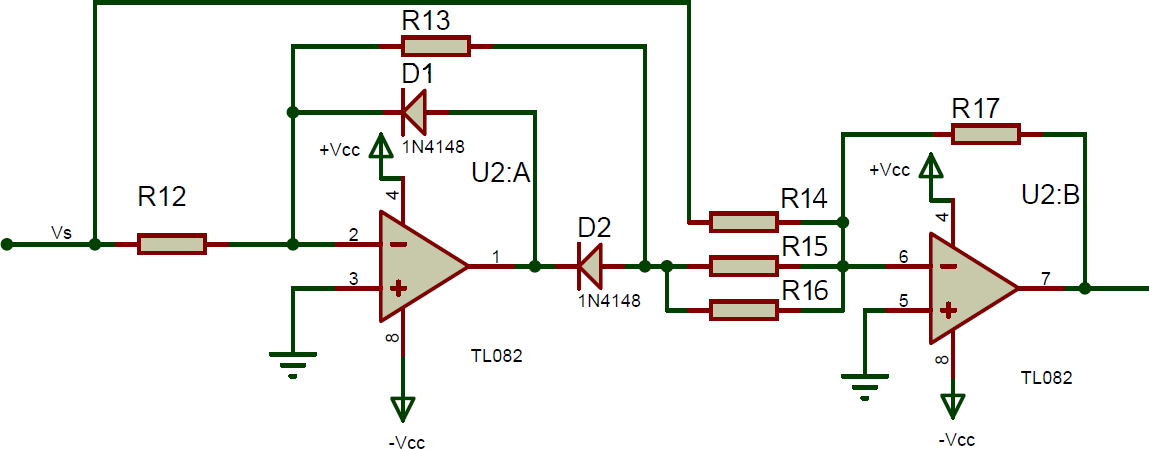
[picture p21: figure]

Figura 17. Esquema de las conexiones de los amplificadores operacionales U2A y U2B (TL082) de la etapa de rectificación.

Como podemos observar en la Figura 17, empleamos un par de diodos 1N4148 como ya hemos mencionado previamente, y diversas resistencias, las cuales compartirán el mismo valor resistivo. A continuación, explicamos el funcionamiento del rectificador empleado mediante el uso de un esquema análogo (Figura 18) para facilitar su comprensión.

Figura 18. Esquema del rectificador de precisión utilizado para el análisis del circuito eléctrico.

Como podemos observar en la imagen anterior, el rectificador de precisión de onda completa utilizado está constituido por dos fases diferenciadas caracterizadas por: un rectificador de precisión de media onda, marcado en rojo; y un circuito sumador, marcado en azul. Los puntos que hemos utilizado para analizar el circuito son los localizados a la entrada y a la salida de la etapa, y el punto A, el cual separa ambas fases. Por último, añadir que hemos simplificado las resistencias en paralelo R15 y R16 en una única resistencia a la que denominamos Rp, siendo su valor:

1 = 1 + 1

→ R15 = R16 = R12 = R13 = R14 = R17 = R → 1

= 1 + 1 = 2

Rp R15

R16

Rp = ¹ R (16)

2

Rp R R R

Una vez conocido todo esto, podemos proceder a la explicación de la configuración utilizada. El circuito mostrado corresponde a la etapa posterior al filtrado paso-bajo de la fase anterior, por lo que a su entrada llega una señal alterna acondicionada de morfología sinusoidal. Durante el semiciclo positivo de dicha señal, la salida del amplificador operacional U2A es negativa al tener este una configuración inversora. Por consiguiente, el diodo D2 se polariza directamente, obteniendo en el punto A una señal con la misma amplitud que la de entrada (VM) pero desfasada 180º. Por otro lado, durante el semiciclo negativo, es el diodo D1 el que se polariza directamente mientras que el diodo D2 se polariza inversamente, impidiendo así el paso de la corriente hasta el punto A, por lo que la señal que recibe en estos momentos dicho punto es nula (Figura 19).

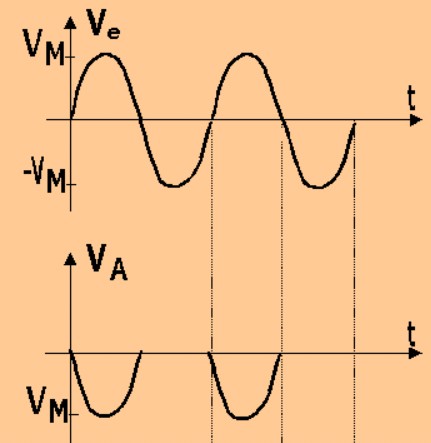
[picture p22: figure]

Figura 19. Esquema de la evolución de la señal de trabajo con el tiempo a la entrada del circuito (Ve) y en el punto A (Va) [16].

En este caso, la señal obtenida a partir de la rectificación de media onda previa consiste en una señal desfasada 180º, y con el doble de amplitud que la excitación original (Figura 20).

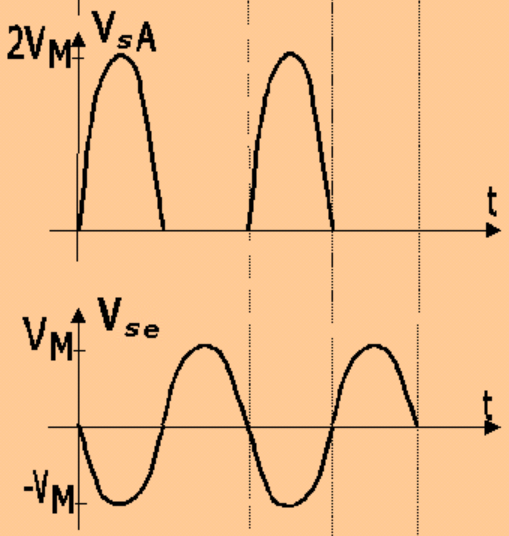
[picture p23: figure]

Figura 20. Esquema de la evolución de las señales generadas en el circuito sumador a partir de la señal de entrada al circuito (abajo) y la recibida del punto A (arriba) [16].

Finalmente, el sumador utiliza ambas señales para obtener una única señal de salida, la cual se obtiene como el resultado de sumar los valores de cada una de las señales en cada instante de tiempo. De esta forma, hemos realizado una rectificación completa de la excitación inicial, obteniendo una señal final que en todo momento describe semiciclos positivos y que mantiene el mismo valor de amplitud que el original (Figura 21).

Figura 21. Esquema de la evolución de la señal rectificada con el tiempo [16].

Como ya hemos mencionado anteriormente, en esta fase del proyecto no se realiza ninguna amplificación de la señal del trabajo. Queremos aclarar, por tanto, que aun habiendo amplificado una de las señales utilizadas en la rectificación, el resultado final es que la ganancia del circuito es 1, por lo que la amplitud permanece constante. Hemos elegido un valor de R = 1 KΩ para todas las resistencias, preferiblemente de baja tolerancia, ya que, de esta forma, mejoramos la exactitud del resultado final de la etapa [16 (https://scuolaelettrica.it/escuelaelectrica/elettronica/differe4.php)].

Por último, debemos aplicar una etapa de filtrado adicional con el objetivo de reducir en lo posible el rizado de la señal obtenida, de forma que nos sea más fácil trabajar con ella [33 (https://es.wikipedia.org/wiki/Rectificador)].

###### 3.3.6. Etapa de filtrado paso-bajo II

La última etapa consiste en un filtrado paso-bajo con la misma configuración que el filtro anterior, pero con la diferencia de que en este caso no queremos realizar ninguna amplificación, por lo que debemos escoger unos valores de resistencia tales que la ganancia final del proceso sea lo más cercana a 1.

En este caso, la frecuencia de corte que hemos seleccionado es de 2 Hz, debido principalmente a las bajas frecuencias de transmisión de las señales bioeléctricas que intervienen en el movimiento muscular, siendo de aproximadamente 1 Hz. Para ello, al igual que en el filtrado anterior, utilizamos la misma tipología de filtro Sallen-Key de segundo orden, aplicando la correspondiente simplificación de utilizar un par de condensadores y de resistencias del mismo valor [13 (http://www.ti.com/lit/an/sloa024b/sloa024b.pdf)]. Igualmente, nos interesa trabajar con una respuesta del tipo Butterworth para que los valores varíen lo menos posible con la frecuencia [12 (http://ocw.uv.es/ingenieria-y-arquitectura/filtros-digitales/tema_2._revision_de_los_tipos_de_filtros_analogicos_mas_comunes.pdf)]. En la Figura 22 podemos apreciar la configuración del filtro utilizado:

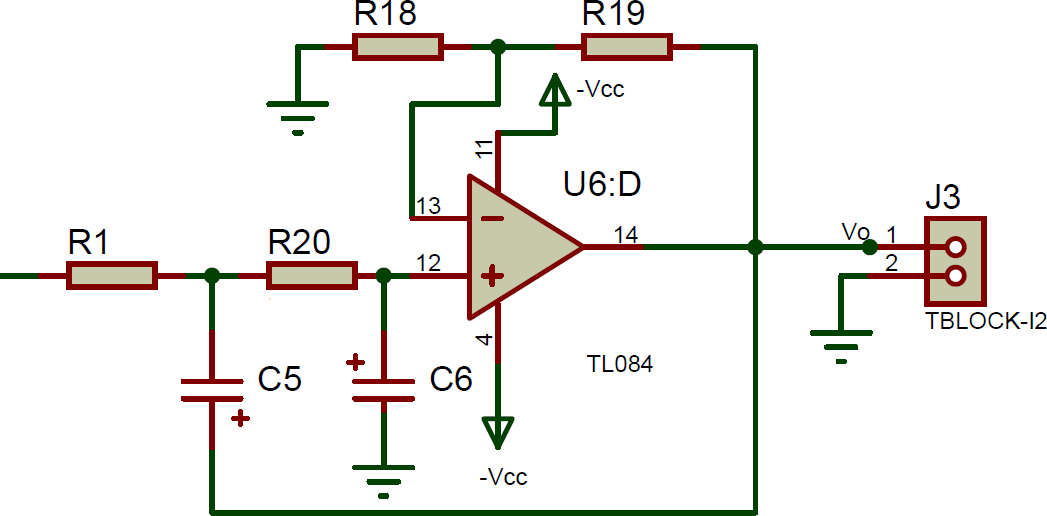
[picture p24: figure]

Figura 22. Esquema de las conexiones del amplificador operacional U6D (TL084) de la etapa de filtrado paso-bajo II.

El principio de funcionamiento de este tipo de filtros es el mismo que hemos explicado anteriormente para el caso de los filtros RC. En esta etapa se aplica un filtrado paso-bajo, por lo que debemos colocar las resistencias en serie con la entrada del amplificador operacional utilizado para permitir así el paso de las señales de baja frecuencia. Las señales cuya frecuencia se sitúa por encima de la frecuencia de corte y que consiguen pasar a través de las resistencias, circulan a través de un condensador, el cual les presenta menor oposición, hacia una toma de tierra, de forma que su intervención en el proceso de filtrado será mínima [9 (http://www.learningaboutelectronics.com/Articulos/Filtro-paso-alto.php)]. Cabe añadir que, para esta etapa, a diferencias de las anteriores, utilizamos condensadores electrolíticos polarizados debido a que son los más convenientes por su relación tamaño/capacidad.

###### 3.3.7. Síntesis del diseño de las etapas de tratamiento

Antes de empezar con la parte experimental, hemos resumido las características principales de las diversas etapas que componen el ciclo de postratamiento. Para ello, utilizamos un cuadro resumen (Tabla 4) para organizar de una forma óptima toda la información básica reunida hasta ahora. Hemos adjuntado además un esquema del circuito final del proyecto diferenciando las dos fases constituyentes (Figuras 23 y 24), donde se puede apreciar mejor el orden y las diversas conexiones entre cada una de las etapas. Podemos visualizar igualmente el diseño global del circuito en el Anexo II.

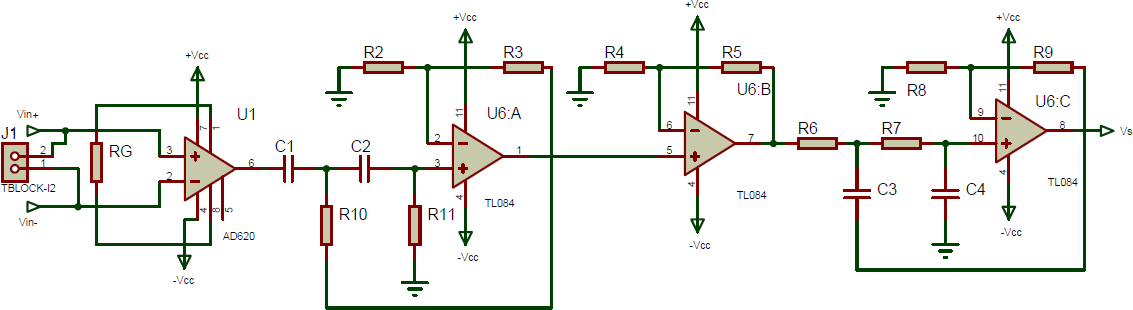
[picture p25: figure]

Figura 23. Esquema global de la fase de acondicionamiento de la señal de entrada.

Figura 24. Esquema global de la fase de obtención de la envolvente de la señal acondicionada.

TRATAMIENTO DE SEÑALES BIOELÉCTRICAS

Fase de acondicionamiento de la señal
Etapa | Componentes | Rango ganancia (V/V) | Función principal
Amplificación diferencial | -Amplificador diferencial AD620 -Resistencia RG = 680 Ω | [66.73; 81.29] | Amplificar la diferencial de potencial entre los electrodos superficiales
Filtrado paso-alto | -Amplif. operacional U6A (TL084) -Resistencia R2 = 680 Ω -Resistencia R3 = 390 Ω -Resistencia R10 = 220 KΩ -Resistencia R11 = 220 KΩ -Condensador C1 = 0.68 µF -Condensador C2 = 0.68 µF | [1.52; 1.63] | Eliminar señales cuyas frecuencias se sitúen por debajo de 1 Hz (consideras como interferencias), y realizar una pequeña amplificación
Amplificación | -Amplif. operacional U6B (TL084) -Resistencia R4 = 3.3 KΩ -Resistencia R5 = 10 KΩ | [3.74; 4.35] | Amplificar la señal recibida un valor suficiente como para acercarse al orden de voltios
Filtrado paso-bajo I | -Amplif. operacional U6C (TL084) -Resistencia R6 = 1.2 KΩ -Resistencia R7 = 1.2 KΩ -Resistencia R8 = 680 Ω -Resistencia R9 = 390 Ω -Condensador C3 = 0.068 µF -Condensador C4 = 0.068 µF | [1.52; 1.63] | Eliminar señales cuyas frecuencias se sitúen por encima de 2 KHz (consideras como interferencias), y realizar una pequeña amplificación

Fase de obtención de la envolvente
Etapa | Componentes | Rango ganancia (V/V) | Función principal
Rectificación | -Amplif. operacional U2A (TL082) -Amplif. operacional U2B (TL082) -Resistencia R12 = 1 KΩ -Resistencia R13 = 1 KΩ -Resistencia R14 = 1 KΩ -Resistencia R15 = 1 KΩ | 1 | Transformar la señal alterna acondicionada de entrada en una señal monopolar, consiguiendo así describir una aproximación de la envolvente de dicha señal

| -Resistencia R14 = 1 KΩ -Resistencia R15 = 1 KΩ -Diodo D1 (1N4148) -Diodo D2 (1N4148)
Filtrado paso-bajo II | -Amplif. operacional U6D (TL084) -Resistencia R1 = 12 KΩ -Resistencia R18 = 100 KΩ -Resistencia R19 = 100 Ω -Resistencia R20 = 12 KΩ -Condensador C5 = 6.8 µF -Condensador C6 = 6.8 µF | 1.001 | Suavizar el rizado de la señal rectificada para obtener de forma más detallada su envolvente característica, permitiendo así su posterior interpretación

Ganancia total del circuito = 744 V/V, con un rango de [577; 940] V/V

Tabla 4. Cuadro resumen de las diferentes etapas que componen el proceso de pos tratamiento.

### 3.4. Interpretación de las señales con Arduino

El último paso del proyecto consiste en analizar las señales tratadas, y para ello utilizamos el entorno de Arduino. Arduino es una compañía que ofrece públicamente una plataforma donde poder realizar diversos sistemas electrónicos de una forma interactiva, sencilla y autodidacta. Generalmente, la mayoría de los trabajos que pueden llevarse a cabo con esta plataforma consisten en la realización de un código informático con el propio software de la compañía, programado en el lenguaje informático C++, para posteriormente transmitirlo a una de las placas que comercializa la empresa, la cual realiza unas funciones determinadas basadas en el código proporcionado [35]. Para ello, dicha placa dispone de una serie de pines de entrada y de salida de información, además de conexiones para alimentarla externamente, y un conector USB para transmitir información entre la placa y el ordenador. Existe la posibilidad de añadir complementos a la propia placa con el fin de ampliar su capacidad para realizar ciertas funciones, sin embargo, para este proyecto únicamente necesitamos la placa. En nuestro caso, hemos optado por escoger el modelo de placa “Arduino UNO R3” (Figura 25), debido a su bajo coste económico comparado con otros modelos que disponen de una mayor cantidad de pines, y a su mayor facilidad de uso.

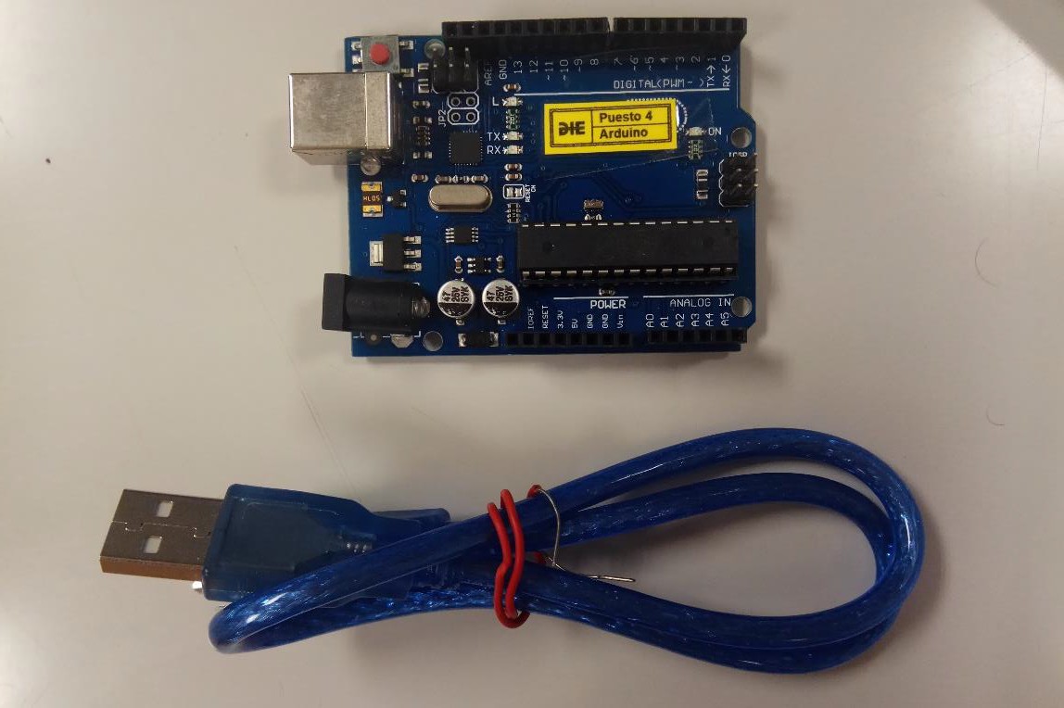
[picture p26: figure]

Figura 25. Placa Arduino UNO R3 con cable USB 2.0 tipo A-B.

Como podemos observar, el modelo elegido consiste en una placa de circuito impreso constituida por diversos componentes electrónicos, la cual dispone de un determinado número de pines definidos de 0 a 13 en caso de tratar señales digitales, y de A0 a A5 en caso de tratar señales analógicas. Cabe añadir que, entre los pines digitales numerados, hay algunos que pueden trabajar con señales analógicas.

Para nuestro proyecto, precisamos de un único pin de entrada analógico, ya que es suficiente para recoger los datos de la señal a analizar. Cuando el código programado recibe los datos de la señal tratada a través del pin elegido, realiza una serie de instrucciones que determina la posición de la mano mediante los movimientos de apertura y cierre de esta. Dichos movimientos se generan a partir de la transmisión de los potenciales de acción descritos en el apartado 2.1. Potencial de acción, los cuales caracterizan las señales bioeléctricas. A partir del análisis de la amplitud de estas señales en el marco temporal, podemos interpretar si nuestra mano se encuentra abierta o cerrada. Por tanto, una vez descritas las características principales de la plataforma de Arduino y los principios del proceso a realizar, procedemos a explicar la creación del código fuente utilizado.

###### 3.4.1. Programación y aplicación del código informático

## 4. Implementación del proceso

Para la realización del proyecto, utilizamos los equipos electrónicos proporcionados por el departamento de electrónica de la universidad. Empleamos una fuente de alimentación para alimentar los diferentes componentes del circuito, un generador de funciones para recrear las señales bioeléctricas del cuerpo, y un osciloscopio para poder visualizar las señales eléctricas tratadas. Además, hemos implementado el circuito diseñado en una placa de pruebas o protoboard, de forma que podemos analizar con mayor facilidad cada etapa del proceso artificial, para posteriormente aplicar el mismo proceso con nuestra placa de circuito impreso y las señales reales.

La fuente de alimentación de la Figura 26 dispone de unos interruptores con los que podemos definir la disposición del voltaje suministrado. En este caso, necesitamos una alimentación de ±9V en serie, el cual se suministra posteriormente con ayuda de unas pilas de 9V para el caso de captación de señales del cuerpo con el fin de asegurar la integridad del individuo.


Figura 26. Fuente de alimentación.

El generador de funciones de la Figura 27 proporciona, en este caso, una señal sinusoidal que debe representar de forma aproximada una bioseñal. Hemos elegido una frecuencia de 10 Hz para la excitación generada, ya que es aproximadamente el valor en el que nuestras señales de trabajo se vuelven más estables.

Figura 27. Generador de funciones.

El siguiente equipo es el osciloscopio (Figura 28), con el cual podemos comprobar el correcto funcionamiento de nuestro circuito. Para ello, utilizamos diversas sondas, cada una de ellas conectada a uno de los cuatro canales de los que dispone el osciloscopio utilizado. Para facilitar el seguimiento del análisis, hemos asignado un canal determinado a cada uno de los procesos que queremos analizar: el canal 1 representa la señal de comprobación de las etapas de filtrado; el canal 2 representa la señal de salida de cada etapa; el canal 3 corresponde a la señal de entrada al circuito, después de pasar por el divisor de voltaje; y el canal 4 corresponde únicamente a la señal de salida de la etapa de rectificación.


Figura 28. Osciloscopio.

Por último, disponemos de la placa de pruebas mostrada en la Figura 29, con la misma distribución de componentes que el circuito empleado en nuestra PCB.


Figura 29. Conexiones de la placa de pruebas utilizada en el tratamiento de señales artificiales.

La señal de entrada de 20 mV se transmite al circuito después de pasar por el divisor de voltaje, consiguiendo así una amplitud de 5 mV, para posteriormente enviar la señal de salida tratada al canal 2 del osciloscopio mediante la sonda correspondiente.

### 4.1. Tratamiento de señales

Como ya hemos mencionado, el proceso se realiza con dos tipos de señales diferentes: primero con señales artificiales obtenidas con el generador de funciones, y luego con señales bioeléctricas del cuerpo. Los resultados de ambos métodos son representados en el osciloscopio, teniendo en cuenta ciertas consideraciones para su interpretación.

Como hemos podido apreciar durante el experimento, las señales mostradas se han visto afectadas ligeramente por interferencias, por lo que contienen una pequeña cantidad de ruido. Debido a esto, los valores de amplitud representados en el osciloscopio pueden no ser exactos, y por ello hemos decidido contrastarlos calculando el valor pico a pico de la señal obtenida con la escala de divisiones vertical, a partir de una propia aproximación de lo que podría ser la morfología de dicha señal sin interferencias. De esta forma, podemos calcular con mayor exactitud la ganancia obtenida en cada etapa de acondicionamiento. Por último, añadir que los valores analizados suelen variar levemente durante el análisis de las señales, sin embargo, esta variación es del orden de unos pocos milivoltios, por lo que hemos considerado los valores medidos como generales.

###### 4.1.1. Señales artificiales

El primer paso es analizar las señales artificiales, ya que tenemos un mayor control sobre los parámetros característicos de estas, pudiendo variar en cualquier momento tanto su frecuencia como su amplitud. En este apartado se comprueba el correcto funcionamiento de las diferentes etapas del circuito, para posteriormente realizar directamente un análisis final de las señales reales en el siguiente apartado.

Para la primera etapa de amplificación diferencial, según los cálculos realizados anteriormente, debemos obtener una ganancia comprendida entre [66.73; 81.29] V/V. Como podemos observar en la Figura 30, el valor de pico a pico de la señal tratada que se muestra en la parte inferior de la pantalla es de 380 mV, por lo que estamos obteniendo una ganancia de:

G = Vs = 380mV = 76 V/V (24)

Ve 5mV

Por otro lado, si calculamos el valor pico a pico mediante las divisiones verticales, resulta:

Vpp = esc · div = 100mV · 3.4 = 340mV (25) Por lo que realizamos una amplificación con una ganancia de:

G = Vs = 340mV = 68 V/V

Ve 5mV

Figura 30. Señal obtenida en la etapa de amplificación diferencial.

En este caso, ambos valores calculados cumplen con los límites de ganancia, por lo que concluimos que la primera etapa funciona correctamente.

Para la segunda etapa de filtrado paso-alto, según los cálculos realizados anteriormente, debemos obtener una ganancia comprendida entre [1.519; 1.634] V/V. Como podemos observar en la Figura 31, el valor de pico a pico de la señal tratada que se muestra en la parte inferior de la pantalla es de 628 mV, por lo que estamos obteniendo una ganancia de:

G = Vs = 628mV = 1.65 V/V

Ve 380mV

Por otro lado, si calculamos el valor pico a pico mediante las divisiones verticales, y teniendo en cuenta esta vez el valor de amplitud de la etapa anterior calculado por este mismo método, resulta:

Vpp = esc · div = 100mV · 5.5 = 550mV

Por lo que realizamos una amplificación con una ganancia de:

G = Vs = 550mV = 1.62 V/V

Ve 340mV


Figura 31. Señal obtenida en la etapa de filtrado paso-alto.

En este caso, el primer resultado excede ligeramente el rango de amplificación calculado previamente. Esto se puede deber a la cantidad de interferencias que intervienen durante el proceso, o a la aproximación de 5 mV realizada en el divisor de tensión inicial. Por todo ello, y teniendo en cuenta que con el segundo método la amplificación aplicada cumple con los límites de ganancia, concluimos que la segunda etapa funciona correctamente. Sin embargo, antes de continuar con el siguiente proceso, debemos aplicar el diagrama de Bode para comprobar que el filtro trabaja con la frecuencia elegida. Dicho diagrama nos permite estudiar la respuesta del sistema en el rango de frecuencias de trabajo, por lo que, para obtener una conclusión, se debe analizar la respuesta de esta etapa variando el valor de la frecuencia de la señal de entrada. El valor de la frecuencia para el cual la ganancia de la etapa es de -3 dB nos indica cuál es la frecuencia de corte del filtro. Esto se debe a que dicho valor de ganancia corresponde a la frecuencia a partir de la cual se produce el mayor orden de filtrado (es decir, la frecuencia de corte), diferenciando notablemente entre la banda de paso y la banda de rechazo características del filtro (Figura 32).

Figura 32. Diagrama de Bode para un filtro paso-bajo (izquierda) y un filtro paso-alto (derecha) [36].

Para calcular la ganancia en decibelios, aplicamos la siguiente expresión:

G [V/V] = Vs → G [dB] = 20 · log(G [V/V]) (26)

Ve

La comprobación del filtro se realiza con una señal de entrada de 2V, ya que si aplicamos una amplitud de menor orden los valores obtenidos están más dispersos. Tras realizar diversas pruebas variando la frecuencia alrededor de un valor cercano a la frecuencia de corte escogida de 1 Hz, se obtienen el siguiente resultado a partir de los valores mostrados en la Figura 33:

G [V/V] = ¹.⁵² → G [dB] = 20 · log(¹.⁵²) = -3.05 dB

2.16 2.16

Tras este resultado, concluimos que la frecuencia de corte del filtro diseñado es de aproximadamente 0.79 Hz, algo inferior a la escogida inicialmente. Igualmente, al ser un valor cercano a la frecuencia de corte elegida lo damos por válido, por lo que se concluye que el filtro paso-alto utilizado funciona correctamente.

Figura 33. Datos recogidos del osciloscopio para una señal de entrada de 2 V y 1 Hz.

Para la tercera etapa de amplificación, según los cálculos realizados anteriormente, debemos obtener una ganancia comprendida entre [3.74; 4.35] V/V. Como podemos observar en la Figura 34, el valor de pico a pico de la señal tratada que se muestra en la parte inferior de la pantalla es de 2.62 V, por lo que estamos obteniendo una ganancia de:

G = Vs = 2620mV = 4.17 V/V

Ve 628mV

Por otro lado, si calculamos el valor pico a pico mediante las divisiones verticales, y teniendo en cuenta el valor de amplitud de la etapa anterior calculado por este mismo método, resulta:

Vpp = esc · div = 500mV · 4.5 = 2250mV Por lo que realizamos una amplificación con una ganancia de:

G = Vs = 2250mV = 4.09 V/V

Ve 550mV


Figura 34. Señal obtenida en la etapa de amplificación.

En este caso, ambos valores calculados cumplen con los límites de ganancia, por lo que concluimos que la tercera etapa funciona correctamente.

Para la cuarta etapa de filtrado paso-bajo, según los cálculos realizados anteriormente, debemos obtener una ganancia comprendida entre [1.519; 1.634] V/V. Como podemos observar en la Figura 35, el valor de pico a pico de la señal tratada que se muestra en la parte inferior de la pantalla es de 3.8 V, por lo que estamos obteniendo una ganancia de:

G = Vs = 3800mV = 1.45 V/V

Ve 2620mV

Por otro lado, si calculamos el valor pico a pico mediante las divisiones verticales, y teniendo en cuenta el valor de amplitud de la etapa anterior calculado por este mismo método, resulta:

Vpp = esc · div = 1V · 3.8 = 3.8V Por lo que realizamos una amplificación con una ganancia de:

G = Vs = 3800mV = 1.65 V/V

Ve 2300mV


Figura 35. Señal obtenida en la etapa de filtrado paso-bajo I.

En este caso, el primer resultado es ligeramente inferior al rango de amplificación calculado previamente, mientras que el segundo es algo superior. Esto se puede deber a la cantidad de interferencias que intervienen durante el proceso, o a la aproximación de 5 mV realizada en el divisor de tensión inicial. Por todo ello, y teniendo en cuenta que un valor medio de ambos resultados cumple con los límites de ganancia, concluimos que la cuarta etapa funciona correctamente. Sin embargo, antes de continuar con el siguiente proceso, debemos aplicar el diagrama de Bode al igual que en el filtrado anterior para comprobar que el filtro trabaja con la frecuencia elegida. La comprobación del filtro se realiza con las mismas pautas aplicadas en el caso anterior, proporcionando igualmente un voltaje de 2 V. Tras realizar diversas pruebas variando la frecuencia alrededor de un valor cercano a la frecuencia de corte escogida de 2 KHz, se obtienen el siguiente resultado a partir de los valores mostrados en la Figura 36:

G [V/V] = ¹.⁴⁸ → G [dB] = 20 · log(¹.⁴⁸) = -2.98 dB

2.08 2.08

Tras este resultado, concluimos que la frecuencia de corte del filtro diseñado es de aproximadamente 2.87 KHz, superior a la escogida inicialmente. Igualmente, al ser un valor cercano a la frecuencia de corte elegida lo damos por válido, por lo que se concluye que el filtro paso-bajo utilizado funciona correctamente.

Figura 36. Datos recogidos del osciloscopio para una señal de entrada de 2 V y 2 KHz.

Con este último proceso, hemos acabado de analizar el proceso de acondicionamiento de la señal, obteniendo una amplificación total de:

G= Vs = 3800mV = 760 V/V

Ve 5mV

Esta ganancia, la cual cumple con el rango calculado previamente de [577; 940] V/V, nos permite trabajar con un voltaje del orden de voltios, por lo que hemos conseguido el objetivo de esta primera fase. La siguiente fase corresponde a la obtención de la envolvente, aplicando primero una rectificación para posteriormente suavizar el rizado de la señal mediante un filtro paso-bajo. El resultado se muestra en la siguiente imagen:


Figura 37. Señal obtenida en la etapa de rectificación (azul oscuro) y en la siguiente etapa de filtrado paso-bajo II (azul celeste).

Como podemos observar en la Figura 37, la rectificación de onda completa se ha realizado correctamente, ya que hemos obtenido una señal que describe continuamente semiciclos positivos en el marco temporal. Además, según la división vertical, podemos comprobar que la amplitud original se mantiene, ya que:

Vpp = esc · div = 500mV · 3.8 = 1900mV

Este valor calculado corresponde a la amplitud de la señal rectificada, el cual debe ser igual a la mitad de la señal anterior. En este caso, podemos concluir que cumple con la condición ya que la señal de entrada era de 3800mV, y, además, de esta forma se ha podido verificar que no se ha realizado ninguna amplificación en esta etapa.

La última etapa a analizar es el filtrado paso-bajo, el cual, como podemos observar en la misma Figura 37, no ha dado un resultado exactamente correcto. La señal obtenida en esta etapa debería situarse por encima se la señal rectificada, lo cual no corresponde con el resultado mostrado en el osciloscopio. La conclusión realizada es que nuestro circuito nos proporciona lo que parece ser un valor medio de la señal final que deberíamos obtener realmente, sin embargo, podemos trabajar igualmente con dicha señal ya que sigue cumpliendo con la función de mostrar la envolvente de la respuesta. Para acabar, al igual que en los filtros anteriores, debemos aplicar el diagrama de Bode para comprobar que el

filtro trabaja con la frecuencia elegida. La comprobación del filtro se realiza con las mismas pautas aplicadas en los casos anteriores, proporcionando igualmente un voltaje de 2 V. Tras realizar diversas pruebas variando la frecuencia alrededor de un valor cercano a la frecuencia de corte escogida de 2 Hz, se obtienen el siguiente resultado a partir de los valores mostrados en la Figura 38:

G [V/V] = ¹.⁴⁰ → G [dB] = 20 · log(¹.⁴⁰) = -3.1 dB

2 2

Tras este resultado, concluimos que la frecuencia de corte del filtro diseñado es de aproximadamente 1.3 Hz, algo inferior a la escogida inicialmente. Igualmente, al ser un valor cercano a la frecuencia de corte elegida lo damos por válido, por lo que se concluye que el filtro paso-bajo utilizado funciona correctamente.


Figura 38. Datos recogidos del osciloscopio para una señal de entrada de 2 V y 2 Hz.

De esta forma, hemos analizado cada una de las etapas del proceso, concluyendo finalmente que el circuito implementado se ha diseñado correctamente, por lo que podemos aplicarlo en el análisis de las señales bioeléctricas.

###### 4.1.2. Señales bioeléctricas

Para este proceso, únicamente necesitamos el osciloscopio para visualizar los resultados, ya que las señales son generadas por el propio cuerpo del individuo, y la alimentación está proporcionada por dos pilas de 9V conectadas en serie. Las señales son recogidas mediante tres electrodos superficiales, dos de ellos colocados sobre el músculo flexor profundo de los dedos, los cuales se conectan a las entradas del amplificador diferencial AD620, y un tercer electrodo localizado cerca del codo, el cual va conectado a la toma a tierra (Figura 39).

Figura 39. Disposición de los electrodos superficiales sobre el brazo derecho del individuo.

Se han seguido las recomendaciones mencionadas en el apartado 2.2.2. Sensores sobre la colocación de los electrodos, aunque se han realizado algunas variaciones para obtener mejores resultados en la toma de señales. Hemos utilizado, además, un gel conductor entre la superficie del sensor en contacto con la piel y la propia piel del individuo, con el fin de reducir la resistencia que presenta la dermis y mejorar la conducción de las señales eléctricas. Las señales son captadas por los sensores y transmitidas al circuito, donde son acondicionadas con el fin de obtener la envolvente de trabajo que pueda representar la intensidad de los potenciales de acción que activan la contracción del músculo a analizar. De esta forma, cada vez que cerramos la mano, la excitación eléctrica que contrae el músculo se representa en el osciloscopio en forma de picos con una amplitud proporcional

a la fuerza aplicada, mientras que cuando abrimos la mano, la intensidad de las señales es mucho menor, por lo que no se muestra ninguna actividad eléctrica en pantalla. Esto se puede observar mejor en la siguiente imagen:

Figura 40. Señales bioeléctricas tras la aplicación del circuito de acondicionamiento.

En la Figura 40 podemos observar la respuesta del circuito ante la variación de la posición de la mano, más exactamente ante la realización de cinco movimientos consecutivos de apertura y cierre de mano. Como ya hemos mencionado, los picos corresponden al momento de cierre, y su amplitud varía en función de la intensidad de la fuerza con la que cerramos la mano. La señal del canal 3 representa, en este caso, la salida de la fase de acondicionamiento, es decir, la señal amplificada sin haber aplicado la rectificación y el último filtrado paso-bajo. Su amplitud final es de 5.2 V, situándose ligeramente por encima del valor máximo posible que se puede obtener con una señal de 5 mV y el rango de ganancias aplicado. Esto se puede deber tanto a las interferencias presentes durante el proceso, a recibir señales bioeléctricas de amplitudes superiores al rango común de este tipo de señales (Tabla 1), a las características del cuerpo del propio individuo, etc. En conclusión, hay una gran cantidad de factores que pueden variar la amplitud final de la respuesta, sin embargo, esto no supone ningún inconveniente a la hora de interpretar dichas señales.

El siguiente paso consiste, por tanto, en transmitir los resultados a la plataforma de Arduino para proceder a su interpretación. Como la señal envolvente obtenida posee una amplitud de 600 mV aproximadamente, puede ser reconocida por el programa utilizado, ya que es lo suficientemente elevada como para poder trabajar con ella.
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

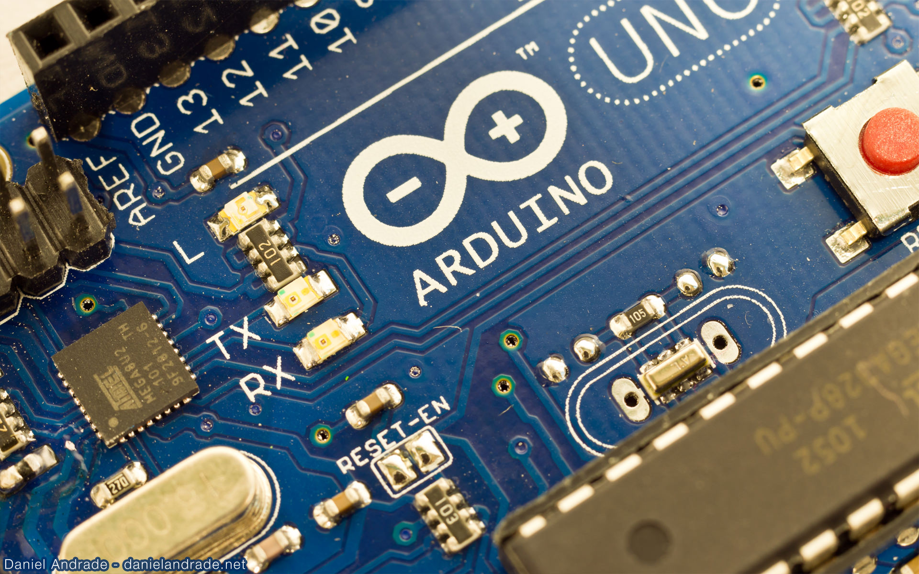
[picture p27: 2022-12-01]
Paguina Web de MARP/Arduino fondo.jpeg

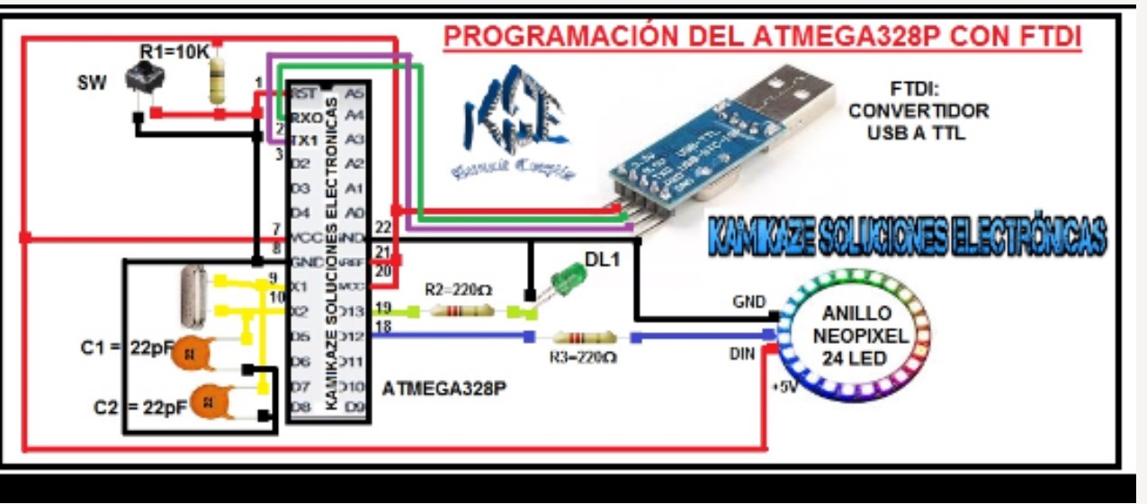
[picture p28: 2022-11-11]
Recursos/Esquema eléctrico bootloader.jpg

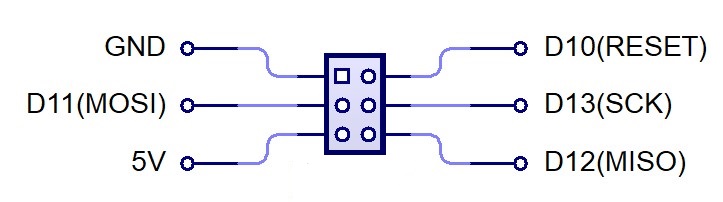
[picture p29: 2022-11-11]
Programador/Conexiones Puerto ISP Externo.jpg

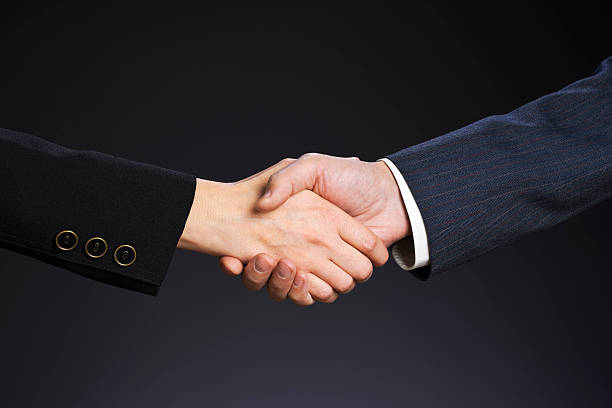
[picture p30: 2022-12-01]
Paguina Web de MARP/Manos saludandose.jpeg

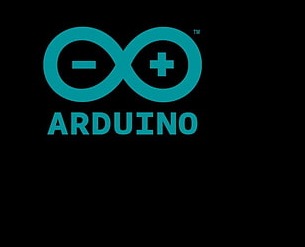
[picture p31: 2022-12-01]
Paguina Web de MARP/Aaaaarduino.jpeg

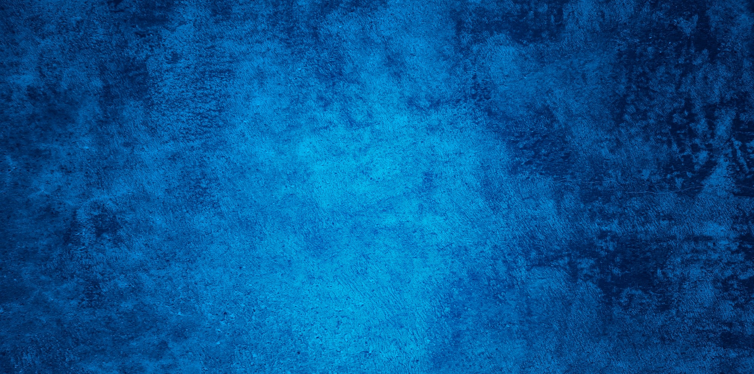
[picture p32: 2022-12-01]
Paguina Web de MARP/fondito.jpeg

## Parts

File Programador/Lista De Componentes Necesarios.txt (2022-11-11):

Lista De Componentes:

1- Arduino Nano Con Pines Dupont Macho.

1- Pines Dupont Hembra Para Soldar Y Hacer La Base Del Arduino.

1- ATMEGA328P O ATMEGA328P-PU (Es Lo Mismo)

1- Base Para IC De 28 Pines.

2- Condensadores Ceramicos 22Pf.

1- Oscilador De Cristal 16Mhz.

1- Condensador Electrolitico 10Uf.

3- Resistencias 220Ohm.

3- Leds (Del Color Que Querais, En Mi Caso Rojo, Verde Y Amarillo).

1- Resistencia De 10K.

1- Placa Perforada Para Soldar.

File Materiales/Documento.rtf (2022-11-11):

Electrodos descartables:
https://articulo.mercadolibre.com.ar/MLA-1101417989-electrodos-descartables-kendall-meditrace-200-x-100-unidades-_JM?matt_tool=75142962&matt_word=&matt_source=google&matt_campaign_id=14240422005&matt_ad_group_id=142508461108&matt_match_type=&matt_network=g&matt_device=c&matt_creative=585527000293&matt_keyword=&matt_ad_position=&matt_ad_type=pla&matt_merchant_id=247758831&matt_product_id=MLA1101417989&matt_product_partition_id=324742923814&matt_target_id=aud-933645523395:pla-324742923814 (https://articulo.mercadolibre.com.ar/MLA-1101417989-electrodos-descartables-kendall-meditrace-200-x-100-unidades-_JM?matt_tool=75142962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)
Programador:
https://articulo.mercadolibre.com.ar/MLA-884826721-programador-pic-usb-k150-grabador-zocalo-zif-cable-_JM#position=5&search_layout=grid&type=item&tracking_id=9883f408-3e1f-4f3c-ba25-28e7ad7c1456
Video de Pads
https://www.youtube.com/watch?v=gmO3hPFXrME
- Que microcontralor nos conviene?
- Sirven los Pads que encontramos como sensores?
- Que programador nos conviene según el Pic elegido?

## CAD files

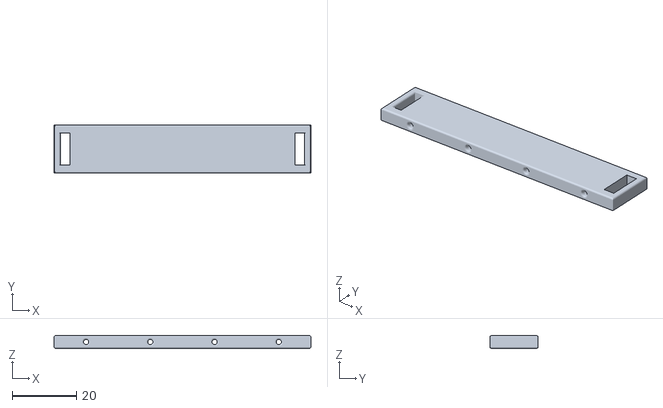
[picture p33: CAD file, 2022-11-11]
autocad/Guias de los hilos.stl
80.0 x 15.0 x 4.00

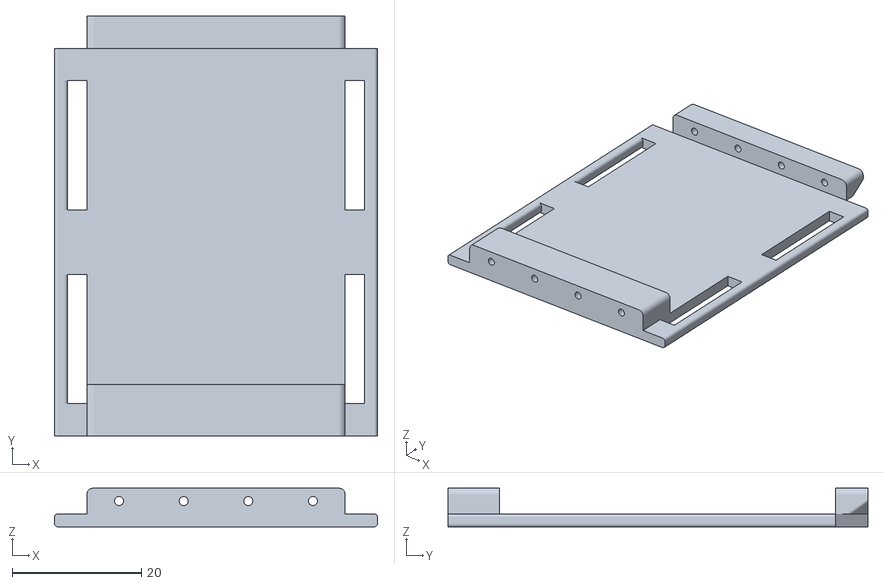
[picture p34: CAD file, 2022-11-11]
autocad/Soporte de resortes.stl
50.0 x 65.0 x 6.00

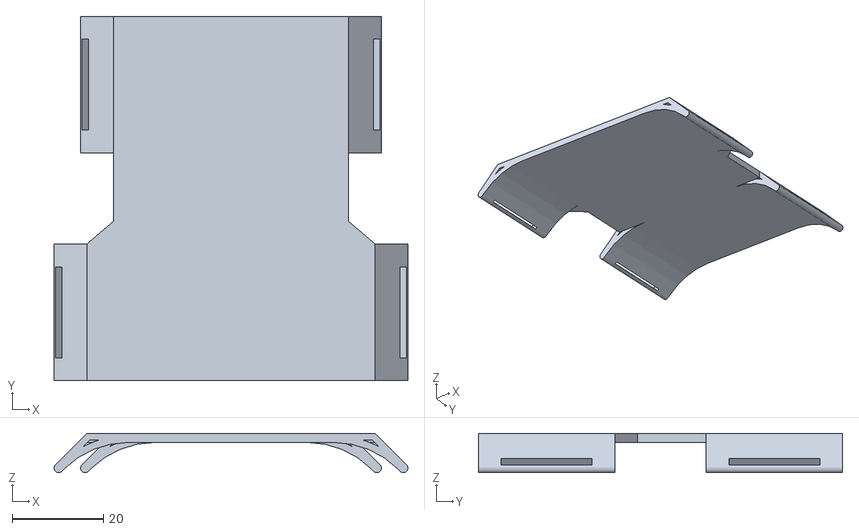
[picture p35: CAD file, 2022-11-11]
autocad/Soporte de Plaqueta.stl
77.8 x 80.0 x 8.66

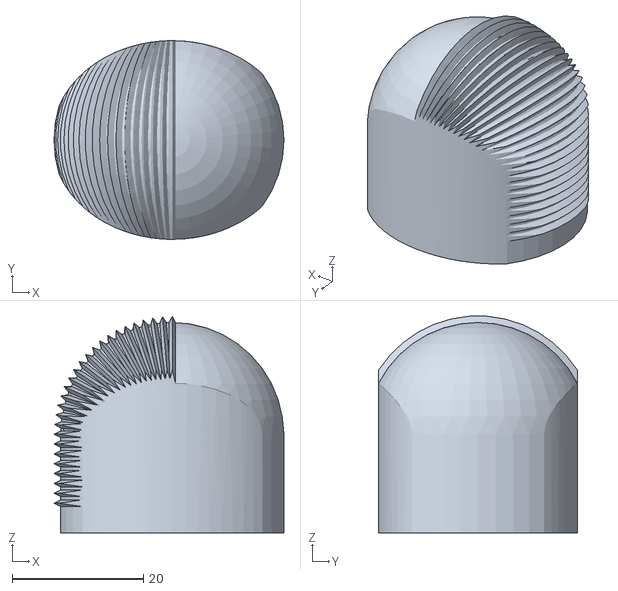
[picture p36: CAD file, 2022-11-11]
autocad/Punta de dedo Marp final.stl
35.0 x 30.2 x 32.9

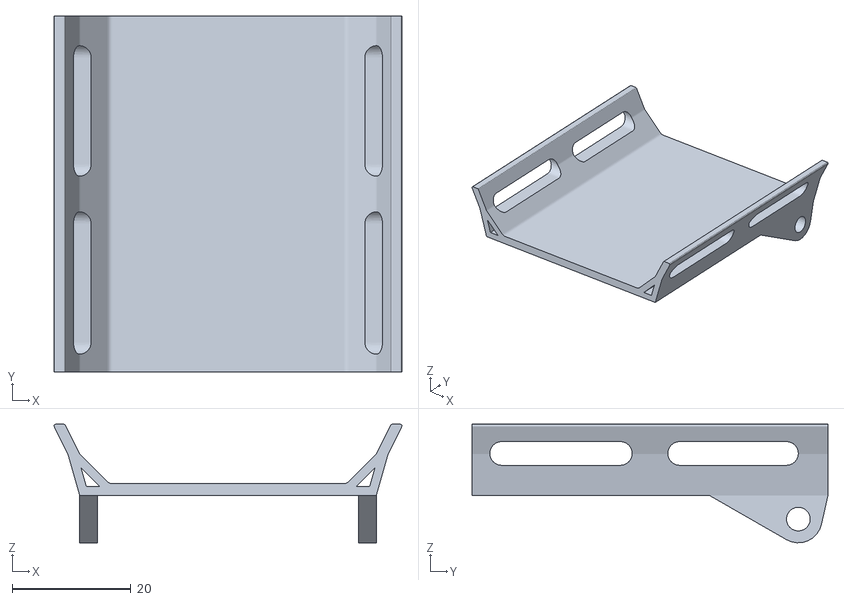
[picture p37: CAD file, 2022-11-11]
autocad/Soporte del motor.stl
58.6 x 60.0 x 20.0

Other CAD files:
Esquema/M.A.R.P.dwg
autocad/logo 3d.dwg
autocad/prueva de anilllo ajustable con flex.dwg
autocad/carcasa.dwg
autocad/Partes del Proyecto exoesqueleto.dwg
autocad/Antebrazo base para microcontrolador.dwg
autocad/Soporte de muñeca para hilos.dwg
autocad/prueva de anillos superiores del dedo.dwg
autocad/Anillos de la mano.dwg
autocad/Cubierta de los dedos.dwg
autocad/Punta de dedo Marp final.dwg

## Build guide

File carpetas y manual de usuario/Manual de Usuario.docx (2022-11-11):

Manual de Usuario

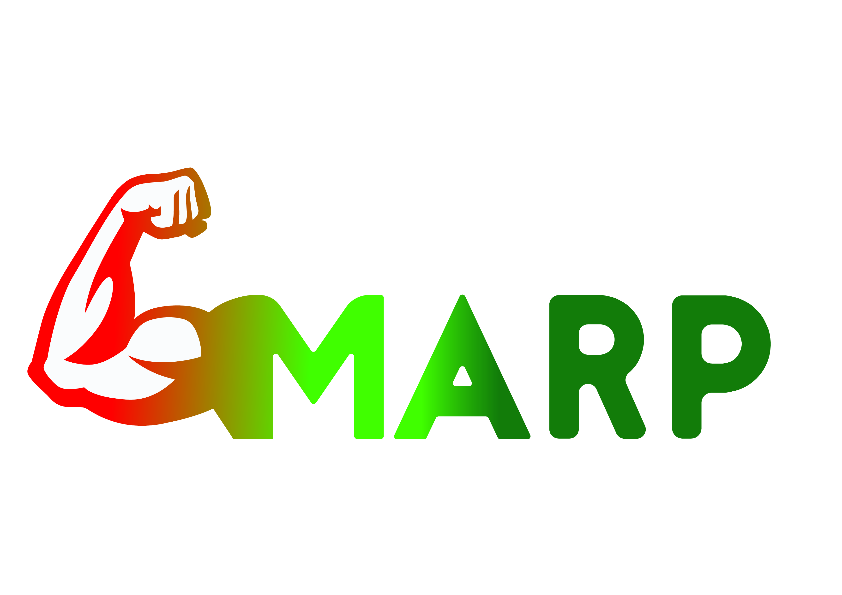
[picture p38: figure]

Índice:

- Información General

- Usos

- Ensamblaje

- Precauciones












Información General

MARP (Mechanical Aid Rehabilitation Prototype) es una ayuda mecánica para la zona de la mano del brazo humano

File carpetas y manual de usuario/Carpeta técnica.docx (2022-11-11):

Proyecto final de 7mo

MECHANICAL
AID
REHABILITATION
PROTOTYPE

Integrantes:

FERNÁNDEZ, Juan Ignacio

LUPICA MARINI, Francisco Joaquín

MONZON MATOS, Thomas Esteban

MONZÓN, Valentín Jeremias Daniel

NIETO, Matías Ezequiel

PIRILLO, Julián Dante

¿Qué es MARP?

M.A.R.P. (Mechanical Aid Rehabilitation Prototype) es el prototipo de un instrumento de rehabilitación de mano para asistir físicamente a pacientes que se puedan encontrar inhabilitados o afectados por fracturas y/o esguinces en accidentes, el cual está diseñado para ofrecer ayuda mecánica mediante movimientos para poder realizar aquellas actividades que se dificultan debido a la situación que están atravesando. Se pueden identificar 4 fases de rehabilitación otorgada por el instrumento:

- Fase de protección: confección de prótesis, manejo de edema y control del dolor.
- Fase restauradora: ejercicios de movilidad activa, activa-asistida y ejercicios de deslizamiento tendinoso.
- Fase de fortalecimiento: ejercicios de resistencia progresiva.
- Fase funcional: enfocada a recuperar habilidades para el desempeño de actividades de la vida diaria y actividades laborales, educativa o de ocio.

Escuela de Educación Secundaria Técnica Nº7 TRQ

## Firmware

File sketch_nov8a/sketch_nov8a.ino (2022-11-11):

#define IN1  11
#define IN2  10
#define IN3  9
#define IN4  8
#define A 12
int Steps = 0;
int Direction = 0;
int number_steps=512;//= 2048/4
void setup()
{
Serial.begin(9600);
pinMode(A, INPUT);
pinMode(IN1, OUTPUT);
pinMode(IN2, OUTPUT);
pinMode(IN3, OUTPUT);
pinMode(IN4, OUTPUT);
// delay(1000);
}
void loop()
{
//1 rotation counter clockwise
if(A<0){
stepper(number_steps);
delay(1000);
//1 rotation clockwise
stepper(-number_steps);
delay(1000);
//Keep track of step number
for(int thisStep=0;thisStep<number_steps;thisStep++){
stepper(1);
}
delay(1000);
for(int thisStep=number_steps;thisStep>0;thisStep--){
stepper(-1);
}
delay(1000);
}
}
void stepper(double nbStep){
if(nbStep>=0){
Direction=1;
}else{
Direction=0;
nbStep=-nbStep;
}
for (int x=0;x<nbStep*8;x++){
switch(Steps){
case 0:
digitalWrite(IN1, LOW);
digitalWrite(IN2, LOW);
digitalWrite(IN3, LOW);
digitalWrite(IN4, HIGH);
break;
case 1:
digitalWrite(IN1, LOW);
digitalWrite(IN2, LOW);
digitalWrite(IN3, HIGH);
digitalWrite(IN4, HIGH);
break;
case 2:
digitalWrite(IN1, LOW);
digitalWrite(IN2, LOW);
digitalWrite(IN3, HIGH);
digitalWrite(IN4, LOW);
break;
case 3:
digitalWrite(IN1, LOW);
digitalWrite(IN2, HIGH);
digitalWrite(IN3, HIGH);
digitalWrite(IN4, LOW);
break;
case 4:
digitalWrite(IN1, LOW);
digitalWrite(IN2, HIGH);
digitalWrite(IN3, LOW);
digitalWrite(IN4, LOW);
break;
case 5:
digitalWrite(IN1, HIGH);
digitalWrite(IN2, HIGH);
digitalWrite(IN3, LOW);
digitalWrite(IN4, LOW);
break;
case 6:
digitalWrite(IN1, HIGH);
digitalWrite(IN2, LOW);
digitalWrite(IN3, LOW);
digitalWrite(IN4, LOW);
break;
case 7:
digitalWrite(IN1, HIGH);
digitalWrite(IN2, LOW);
digitalWrite(IN3, LOW);
digitalWrite(IN4, HIGH);
break;
default:
digitalWrite(IN1, LOW);
digitalWrite(IN2, LOW);
digitalWrite(IN3, LOW);
digitalWrite(IN4, LOW);
break;
}
delayMicroseconds(1000);
if(Direction==1){ Steps++;}
if(Direction==0){ Steps--; }
if(Steps>7){Steps=0;}
if(Steps<0){Steps=7; }
}
}

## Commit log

2022-04-29 docs: incorporar estructura de presentacion (#1)
    * docs: agregar subtitulo
    * docs: agregar subtitulos
    * docs: agregar titulo integrantes
2022-04-29 docs: incorporar nombres de integrantes
2022-05-13 Docs: agregar en que consiste
    agregamos en que consiste
2022-05-13 docs: actualizar en que consiste (#7)
    * Doc: agregar en que consiste
    * Update README.md
2022-12-02 Eliminacion de Pagina Web Boceto
